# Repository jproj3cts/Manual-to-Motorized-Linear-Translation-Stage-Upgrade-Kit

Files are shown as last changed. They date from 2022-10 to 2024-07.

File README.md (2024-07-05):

# Manual-to-Motorized-Linear-Translation-Stage-Upgrade-Kit, using the 28BYJ-48 stepper motor and a heat shrink flexure.
The cheapest possible design for upgrading a manual linear translation stage to an automatic one, whilst retaining the original precision of the device. 

## Intro

This guide should walk you through the conversion of a manual linear translation stage to an automatic one, with a material cost on the order of ~$20. This is very economial considering the typical price of a motorised translation stage is around $1000, 4x that of the manual one.

It can also serve as a tutorial on how to remotely control a ramped 28BYJ-48 stepper motor over wifi, via a website hosted on a Pi Pico W. This is likely a more general use case. If this is what you would like to do, then simply skip the Mouinting Components and Connecting the Flexure section of this guide.

By the time you have finished this guide you should have something vaguely resembling this final product.
### The Final Product

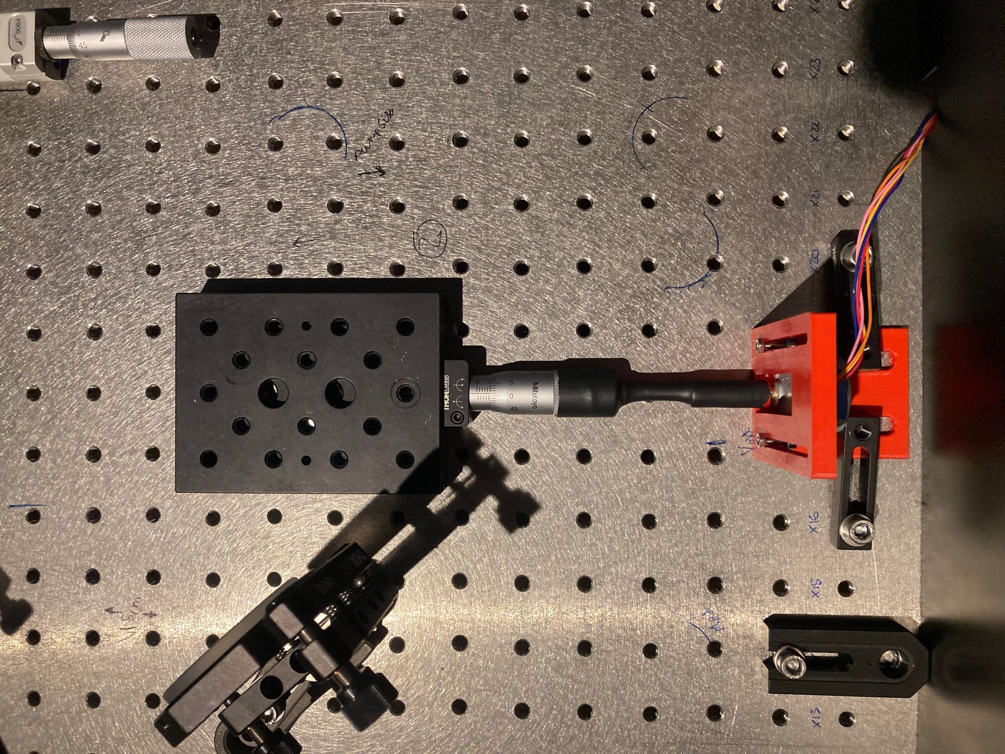
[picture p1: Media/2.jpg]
the Final Product The Final Product


## BILL OF MATERIALS
  ```
  Raspberry Pi Pico W
  28BYJ-48 stepper motor, 1/16th reduction (or equivalent)
  A suitable stepper motor driver board (this guide references the driver board in this pack: https://thepihut.com/products/stepper-motor-driver-pack)
  A suitable plastic project box (metal cannot be used as it will block wifi connectivity)
  USB A to Micro USB 2.0 cable
  20 mm diameter heat shrink
  ```
  
## Electrical Connections

Connect the Pico to the driver board like so. This can be done with solder or jumper wires. I recommend soldering for a more rugged connection.

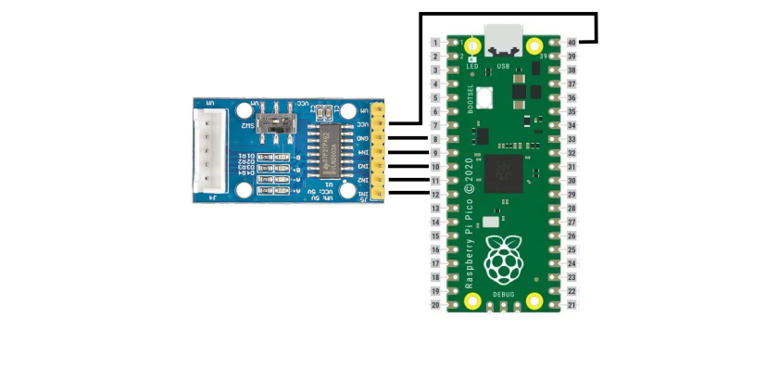
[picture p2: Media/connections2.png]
connections


After this, mount the boards in your project box, making sure to cut holes to allow the usb cable to plug into the Pico and the stepper motor cable to plug into the driver board. You could mount the components with screws but, considering how cheap they are, hot gluing them directly into the project box works just as well.

When powering the device in situ, the usb can be plugged into either a plug to USB transformer or a computer USB port; both should be more than capable of providing the current needed to power the stepper.
  
## Programing the Pico

This project is designed to work with micropython so first set the pico up for that. A good guide for this is available here: https://www.raspberrypi.com/documentation/microcontrollers/micropython.html.

The networking aspect of this device is based off tinyweb (https://github.com/belyalov/tinyweb), so ensure that the tinyweb folder and logging.py file are uploaded the Pi Pico before uploading the boot.py script. This can be done using a Pico compatable IDE like Thonny (https://thonny.org/).

boot.py contains options for changing the SSID and password of the network access point, change those to suit. There are also options for changing settings for how quickly the speed of the stepper motor ramps up and down when it starts and stops. Adjusting these can be helpful if you find the intertia of your motor's load is causing missed steps, leading to inaccuracies in positioning.

## Mounting Components and Connecting the Flexure

If you have chosen to print one of the provided L-brackets, the motor can be mounted to them at an adjustable height using M4 sized bolts. The bracket itself can then be mounted to a table or platform with M6 bolts. 

After, one of the padded linkages should be attatched to the brass protusion from the motor. Which size you will need will vary depending on your printer and settings so I suggest printing all of them and trying each to find which one has the snuggest fit. The ideal case is a linkage that will only go on when hammered lightly with a soft mallet, as it is the least likely to move. 

Next, stretch the heatshrink over both the linkage and the micrometer of the translation stage. Then heat with a heat gun or soldering iron. Make sure to hold the motor and micrometer level as it sets and take care not to melt the 3D printed parts.

The heatshrink is suprisingly ridgid in the rotational direction and has no problem transmitting force to the micrometer, whilst being flexible in the x-y plane. As a result, the axis of rotation of the motor and micrometer can be displaced up to ~5mm, as shown below, without any negative effects.

### The Flexure Connection

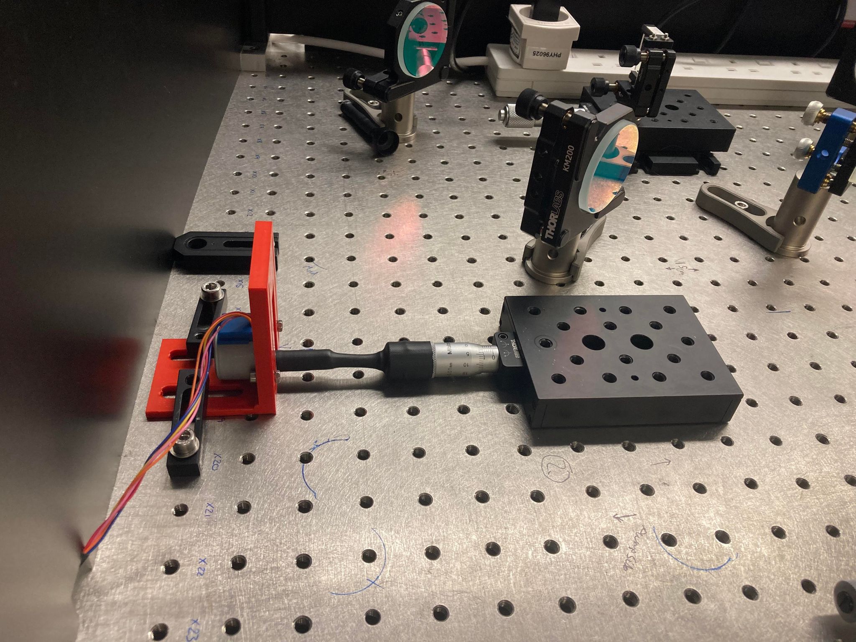
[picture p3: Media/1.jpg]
Connection


### Alternative Connection: Gears
Alternatively, the motor and micrometer can be connected using push fit gears. An easy way to fabricate these would be to laser cut them from acrylic sheet. If you would like to do this, the design files for said gears are provided in the design folder. The slot in the motor mounted gear is deliberately undersized so it can be filed to a close push fit and the inner diameter of the micrometer gear should be adjusted for the specific micrometer you see using.

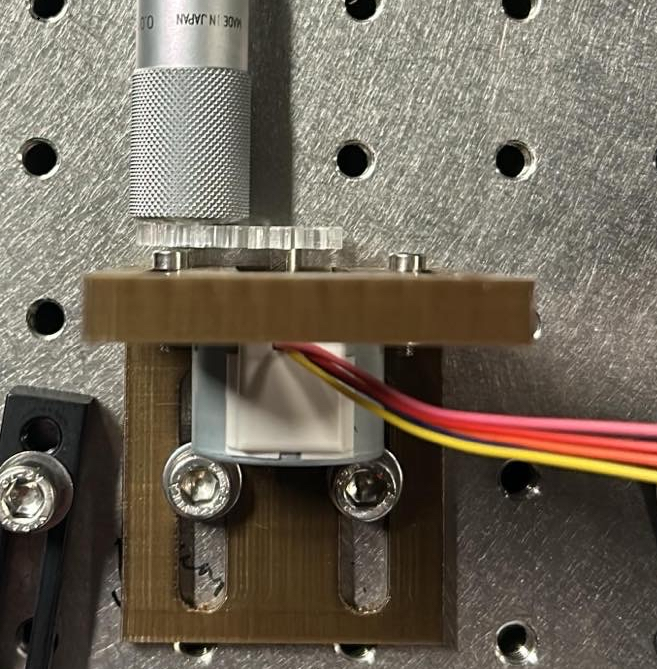
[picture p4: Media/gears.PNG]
Gears


The use of gears requires a correction if swapping directions as the motor needs to travel an extra distance before then coming into contact with the adjacent spoke. This correction is included in the variants of the system.

## Device Operation

After powering the pico, the device should automatically produce it's own wireles access point that can be connected to with a phone or computer in the usual way. After this, open any web browser and enter 192.168.4.1. This will take you to a form that will allow you to control the motor remotely.

This process can be automated by connecting to 192.168.4.1?steps=N, where N is the number of steps (+ve or -ve) you wish to progress. This can be done in python using the urllib library.

### A gif demonstrating the precision of the system (going from 0.5 to 0.5 on the micrometer).

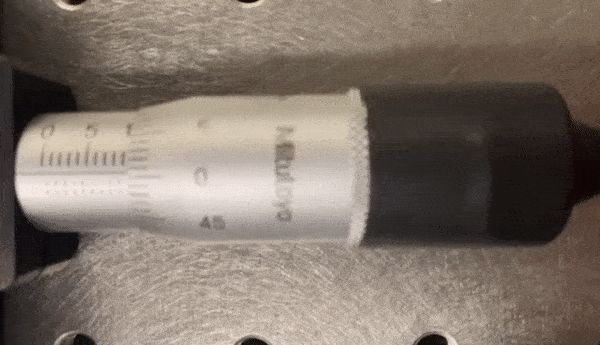
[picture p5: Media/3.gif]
gif


This reliability is sustainable over many rotations. In A recent test the micrometer was rotated 20 times forward then 20 back repeatedly for a total of 800 rotations whilst maintaining a stop position at 0.5 the entire time. 

## Variants of The System
Four variants of this system have already been produce and the code to run them is available in the Variant-code file. A brief explanation/tutorial on both of them is available below.
### Multiple Motors

### Many Wirelessly Networked Motors
This variant uses all the same files as before but a new boot.py script as found in the networked-motor driver. It connects to the first device's wifi using the same wifi name and password. Then it can be controlled wirelessly by an additional device by entering the ip address of the new device into a web browser.

### Step Tracking for the Prevention of Over-Extention of the Micrometer
This code allows for the current position of the micrometer to be stored in a textfile and read and updated while making sure that it does not go out of bounds. A textfile is used rather than a variable in the code, allowing for the device to be switched on and off without losing its step count.

When first setting this up, it is important to enter the correct position on the tracking textfile, converting position to steps. This takes just a single number as shown in the example tracking.txt. For the 25mm micrometer, it has been set so that the 0 point is at 0.5mm (one rotation from 0mm) and the maximum is at 24.5mm which corresponds to 24576 steps. These bounds can be changed. Additionally, moving the motor clockwise (when attached by heat shrink or similar) reduces the amount on the micrometer so the f_step function minuses steps and therefore has the lower bound rather than upper. Therefore b_step is opposite to this.

Care needs to be taken when instead using gears and moving the motor clockwise moves the micrometer anti-clockwise so f_step and b_step do the opposite. In order to rectify this, you can either swap them so f_step is now minus or swap the bounds around and the + and - in new_pos.

### Gear-Correction
As briefly mentioned above the use of gears can cause issues when swapping directions as some of the inputted steps are then used to move the motor to touch the adjacent spoke. For the gears described and a motor which has 512 steps per rotation, this extra distance is 20 steps however it is recommended to callibrate this with your own system.

This code also includes the Step Tracker, making sure that the steps added for the correction are then not added to the Step Tracker as they have not moved the micrometer however with simple adaption, this step tracker can be removed. 

An additional textfile is needed (called 'direction.txt' as specified in code) to store the previous rotation direction, using f or b. It then reads the textfile to identify if the direction is changed and adds the correction to the steps and updates the textfile accordingly. Since this code is applicable to the motor, the bounds have also been swapped as detailed in the Step-Tracking section since clockwise rotation of the motor corresponds to an anti-clockwise rotation of the micrometer.

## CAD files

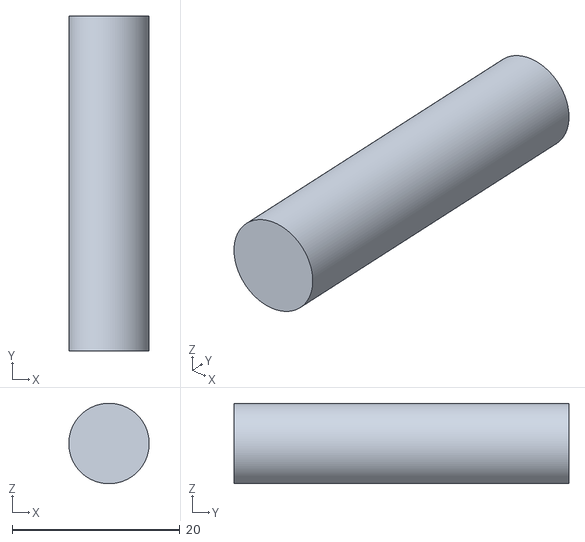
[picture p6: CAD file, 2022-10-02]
3D printing/0.3padlinkage.stl
9.60 x 40.0 x 9.60

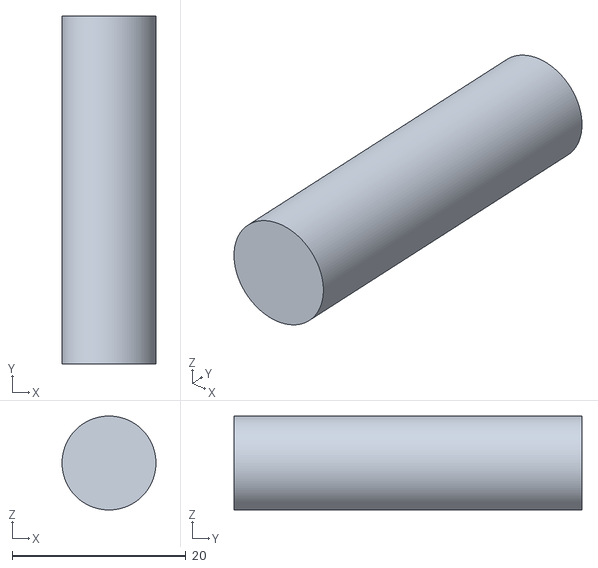
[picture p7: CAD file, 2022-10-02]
3D printing/0.9padlinkage.stl
10.8 x 40.0 x 10.8

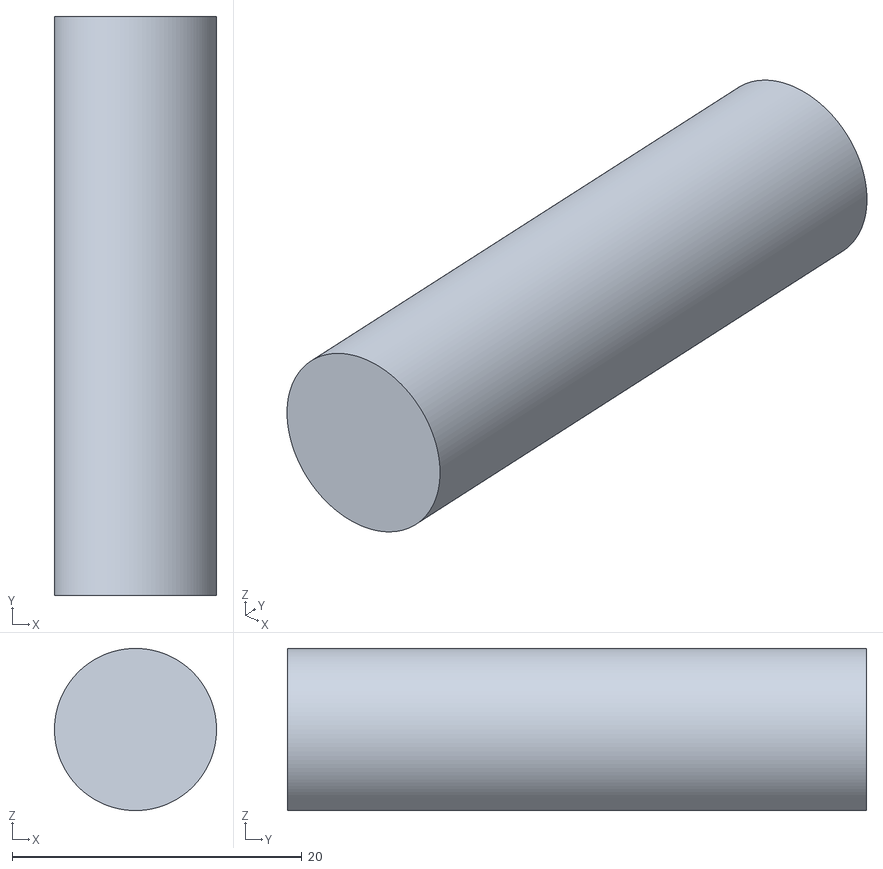
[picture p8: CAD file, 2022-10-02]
3D printing/1.1padlinkage.stl
11.2 x 40.0 x 11.2

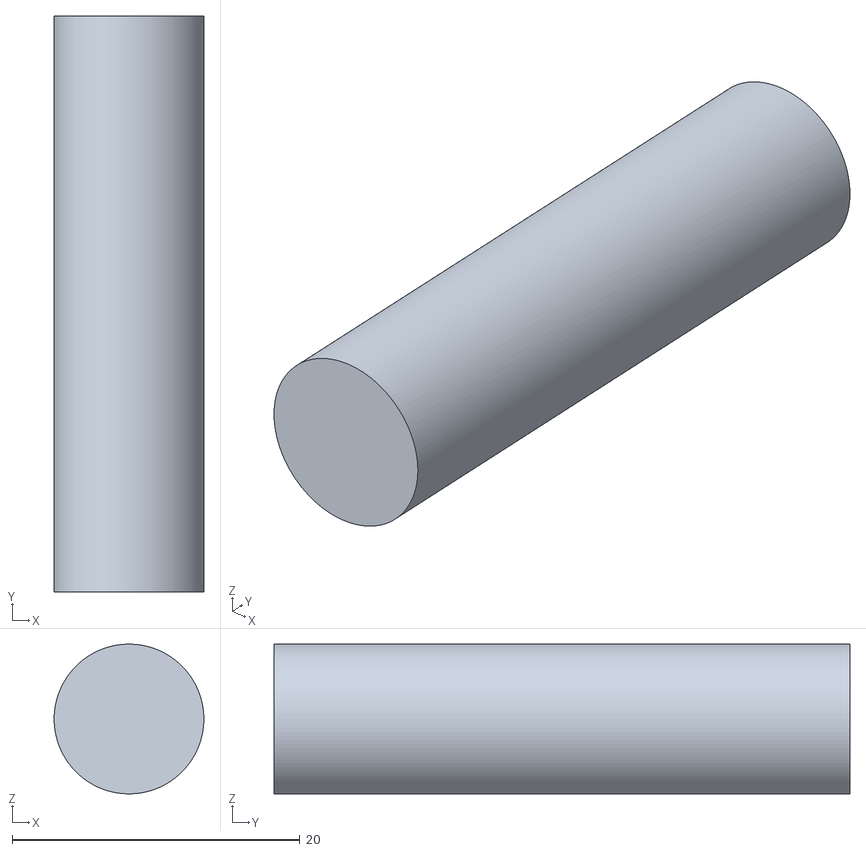
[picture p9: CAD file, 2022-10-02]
3D printing/0.7padlinkage.stl
10.4 x 40.0 x 10.4

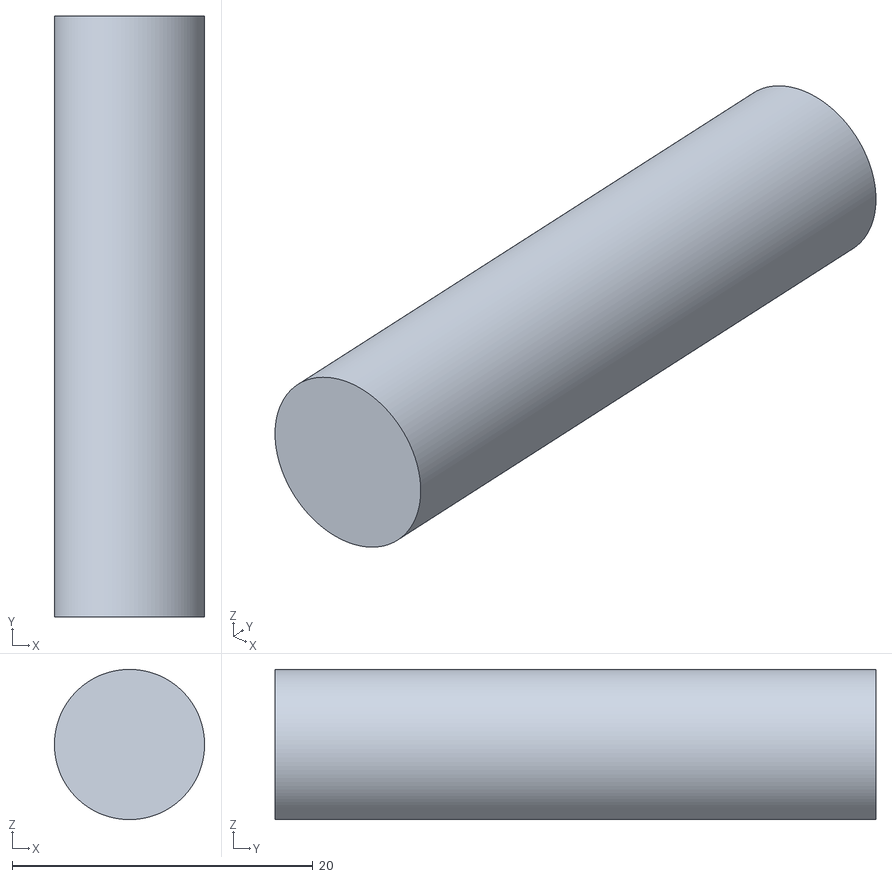
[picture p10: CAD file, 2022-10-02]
3D printing/0.5padlinkage.stl
10.0 x 40.0 x 10.0

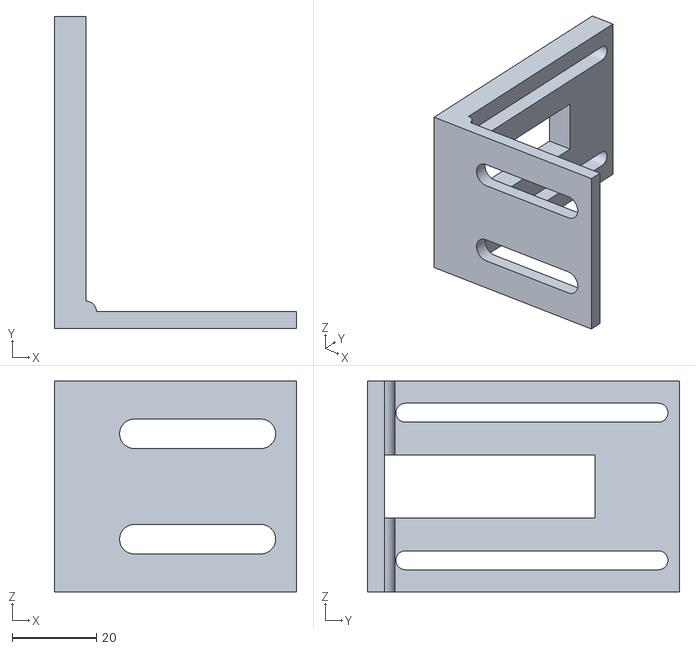
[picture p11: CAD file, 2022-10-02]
3D printing/lbracket.stl
57.5 x 74.0 x 50.0

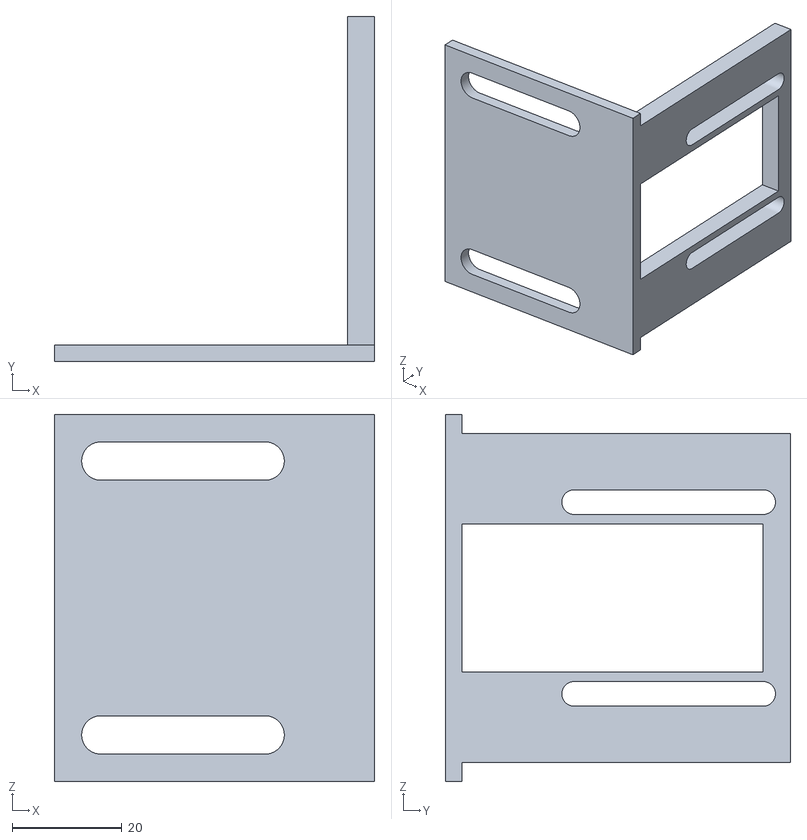
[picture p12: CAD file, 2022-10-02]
3D printing/lBracketWide.stl
58.5 x 63.0 x 67.0

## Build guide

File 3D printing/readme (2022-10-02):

The L bracket files here automatically display on their side, when printing they should be orinetated such that the thin side of the L is face down.

The linkages are presented with a variety of paddings. Depending on your printer and settings, one of these will be optimal for coupling to the 28BYJ-48 stepper motor.

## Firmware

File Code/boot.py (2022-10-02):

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
#To wirelessly control access 192.168.4.1 while connected to the access point.

# Define SSID and password for the access point.
ssid = "YOUR_NEWORKNAME_HERE"
password = "YOUR_PASSWORD_HERE"

# Settings for stepper motor ramp.
dmin=0.002
dstart=0.003
gradient=0.0001

from machine import Pin
from time import sleep
import socket
import network
import tinyweb


# Hardware.
p2 = Pin(6, Pin.OUT)
p3 = Pin(7, Pin.OUT)
p4 = Pin(8, Pin.OUT)
p5 = Pin(9, Pin.OUT)

def f_step(n,dmin=0.002,dstart=0.003,gradient=0.0001):
    # 512 is one rotation.
    # dmin defines shortest time between motor steps, dstart is intial time between steps as well as the end time, and gradient defines the linear ramp up and down between these values.
    ramp_up = True
    ramp_down = False
    for i in range(n):
        # Check if ramp down required to reach starting speed with number of steps left.
        if (n-i)*gradient + dmin <= dstart:
            ramp_down = True
            ramp_up = False
            ioffset = i
        # Ramp up logic.
        if ramp_up == True:
            dt = dstart - gradient*i
            # Check if min step time (max speed) reached, finishing ramp up
            if dt <= dmin:
                ramp_up = False
        # Ramp down logic.
        elif ramp_down == True:
            dt = dmin + gradient*(i-ioffset)
        else:
            dt = dmin

        sleep(dt)
        p2.on()
        p3.off()
        p4.off()
        p5.off()
        
        sleep(dt)
        p2.off()
        p3.on()
        p4.off()
        p5.off()

        sleep(dt)
        p2.off()
        p3.off()
        p4.on()
        p5.off()
        
        sleep(dt)
        p2.off()
        p3.off()
        p4.off()
        p5.on()
        
    sleep(dmin)
    p2.off()
    p3.off()
    p4.off()
    p5.off()
    
def b_step(n,dmin=0.002,dstart=0.003,gradient=0.0001):
    #512 steps is one rotation
    # dmin defines shortest time between motor steps, dstart is intial time between steps as well as the end time, and gradient defines the linear ramp up and down between these values.
    ramp_up = True
    ramp_down = False
    for i in range(n):
        # Check if ramp down required to reach starting speed with number of steps left.
        if (n-i)*gradient + dmin <= dstart:
            ramp_down = True
            ramp_up = False
            ioffset = i
        # Ramp up logic.
        if ramp_up == True:
            dt = dstart - gradient*i
            # Check if min step time (max speed) reached, finishing ramp up
            if dt <= dmin:
                ramp_up = False
        # Ramp down logic.
        elif ramp_down == True:
            dt = dmin + gradient*(i-ioffset)
        else:
            dt = dmin

        sleep(dt)
        p2.off()
        p3.off()
        p4.off()
        p5.on()
        
        sleep(dt)
        p2.off()
        p3.off()
        p4.on()
        p5.off()
        
        sleep(dt)
        p2.off()
        p3.on()
        p4.off()
        p5.off()
        
        sleep(dt)
        p2.on()
        p3.off()
        p4.off()
        p5.off()
        
    sleep(dmin)
    p2.off()
    p3.off()
    p4.off()
    p5.off()


# The following HTML defines the webpage that is served.
html = """<!DOCTYPE html><html>
<head><meta name="viewport" content="width=device-width, initial-scale=1">
</head>
<body><center><h1>Stepper Motor Controller</h1></center><br><br>
<form><center>
<center> <label for="steps">Steps:</label><br> <input type="number" id="fname" name="steps" value="0"><br>
<br><br>
<br><br>
<p>512 steps is equal to 360 degrees; postive numbers are clockwise rotations and negative are anticlockwise rotations.<p></body></html>
</html>
"""

# Define an access point, name it and then activate.
ap = network.WLAN(network.AP_IF)
ap.config(essid=ssid, password=password)
ap.active(True)

# Wait until it is active.
while ap.active == False:
    pass

print("Access point active")
# Print out IP information.
print(ap.ifconfig())

# Start up a tiny web server.
app = tinyweb.webserver()

@app.route('/')
async def index(request, response):
    # Start HTTP response with content-type text/html.
    await response.start_html()
    # Send actual HTML page.
    await response.send(html)
    
    print("Client connected")
    try:
        steps = int(request.query_string[6:])
    except:
        steps = 0
    if abs(steps) < 5120:
        if steps > 0:
            f_step(steps, dmin, dstart, gradient)
        elif steps < 0:
            b_step(abs(steps), dmin, dstart, gradient)

# Run the web server as the sole process.
app.run(host="0.0.0.0", port=80)

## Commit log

2022-10-02 Create 3D printing
2024-07-05 Add files via upload
    For additional raspberry pi pico w used to connect to the first device via wifi and then host its own web server to control the motor.
2024-07-05 Update README.md
    added gear correction section

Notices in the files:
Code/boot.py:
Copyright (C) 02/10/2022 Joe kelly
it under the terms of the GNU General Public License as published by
